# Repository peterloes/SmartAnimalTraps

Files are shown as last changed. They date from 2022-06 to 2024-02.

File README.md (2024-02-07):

# SmartAnimalTraps
Electrical applications for non-deadly animal traps built up with intelligent radio module, drive electronics for servomotors
(flap drive) and drive electronics for different low power light barriers.

Author: Loës P. (2022) 

## 1 RadiomoduleV1.0 & electronicsLightbarriers & electronicsServo
- Radio module V1.0 add-on board (not illustrated)
- Electronic light barriers for different distances.
- Servomotor and shutter is adjusted to the end positions.

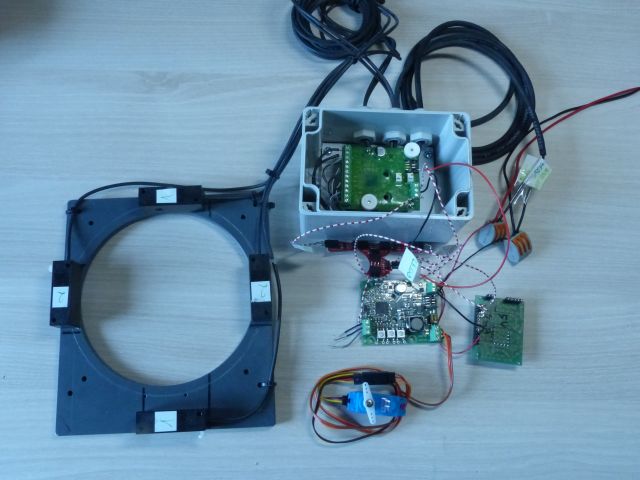
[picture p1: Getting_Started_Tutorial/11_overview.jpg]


The radio handheld transmitter is able to open and close the shutter by pressing a button.

Light barrier 1 and light barrier 2 are connected with logic AND. Both light barriers needs a falling edge of the signals to close the shutter. 
Light barrier 1 and light barrier 2 is forbidden to open the shutter.

Pushbutton 1 and pushbutton 2, mounted on the top of the electronical circuit, are able to open and close the shutter.

### Current consumption:

Standby 20.8mA@6V, clocked approx. 2.0mA@6V (after 10 minutes).

Operate mode 320mA@6V (max.)

### Application bird trap:

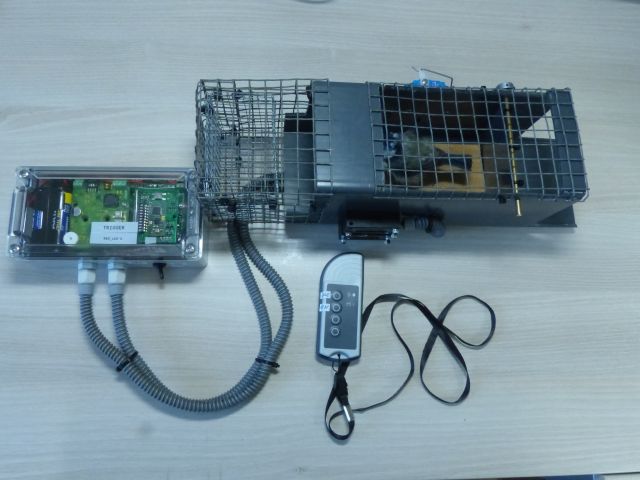
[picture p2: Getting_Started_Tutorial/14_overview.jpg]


### Components:

https://github.com/peterloes/SmartAnimalTraps/blob/main/Getting_Started_Tutorial/13_wireless_radiomodule.JPG

https://github.com/peterloes/SmartAnimalTraps/blob/main/Schematics/radio_module_V1.0.brd.pdf

https://github.com/peterloes/Light_Barrier

https://github.com/peterloes/Servo_Engine

--> Protection against misuse!!! Dear follower, please contact me via email to get more information about the used wireless radio module. 

## 2 RadiomoduleV2.0 & electronicsServo
- Radio module V2.0 add-on board (not illustrated) 
- No light barriers
- Servomotor and shutter is adjusted to the end positions.

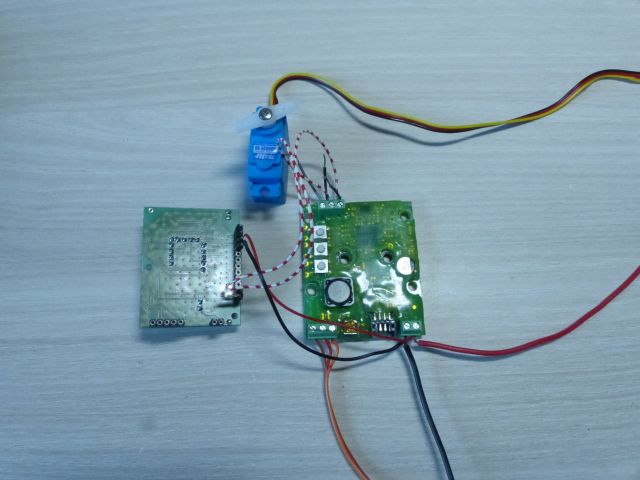
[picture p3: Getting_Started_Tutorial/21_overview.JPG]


The radio handheld transmitter is able to open and close the shutter by pressing a button.

Pushbutton 1 and pushbutton 2, mounted on the top of the electronical circuit, are able to open and close the shutter.

### Current consumption:  

Standby 20.5mA@6V, clocked approx. 2.3mA@6V (after 10 minutes).

Operate mode 235mA@6V (max.)

### Components:

https://github.com/peterloes/SmartAnimalTraps/blob/main/Getting_Started_Tutorial/13_wireless_radiomodule.JPG

https://github.com/peterloes/SmartAnimalTraps/blob/main/Schematics/radio_module_V2.0.brd.pdf

https://github.com/peterloes/Servo_Engine

--> Protection against misuse!!! Dear follower, please contact me via email to get more information about the used wireless radio module. 

## 3 RadiomoduleV3.0 & modifiedServo
- Radio module V3.0 add-on board (Version from year 2010, to revision)
- No light barriers
- Full rotation of modified servomotor --> Motor rotation 360° --> left/right rotations

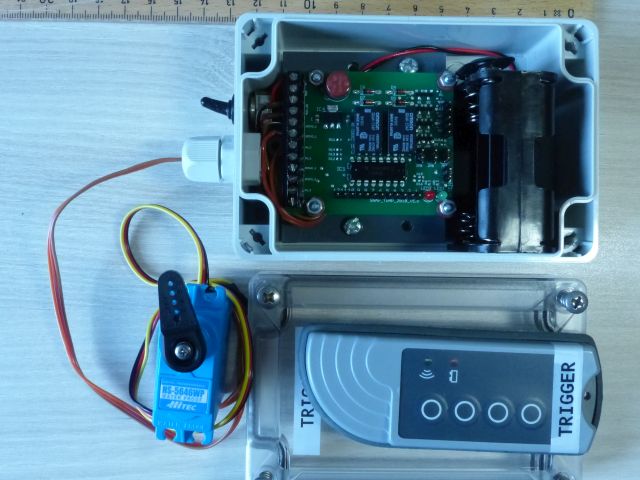
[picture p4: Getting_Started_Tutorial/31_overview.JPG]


The radio handheld transmitter is able to open, close and to rotates the shutter by pressing a button.

### Current consumption:  

Standby 30mA@6V, clocked approx. 11.4mA@6V (after 10 minutes). With LEDs.

Operate mode 179mA@6V Motor is steady turning. With LEDs.

### Application:

https://github.com/peterloes/SmartAnimalTraps/blob/main/Getting_Started_Tutorial/Snaptrap.jpg

### Components:

https://github.com/peterloes/SmartAnimalTraps/blob/main/Getting_Started_Tutorial/13_wireless_radiomodule.JPG

https://github.com/peterloes/SmartAnimalTraps/blob/main/Schematics/radio_module_V3.0.brd.pdf

https://github.com/peterloes/SmartAnimalTraps/blob/main/Getting_Started_Tutorial/33_Servo_modified.JPG

https://github.com/peterloes/SmartAnimalTraps/blob/main/Getting_Started_Tutorial/34_old_batterypack.JPG

--> Protection against misuse!!! Dear follower, please contact me via email to get more information about the used wireless radio module. 

## 4 RadiomoduleV4.0 & reusedFrontplate & electronicsLightbarriers & electronicsServo
- Radio module V4.0 add-on board (not illustrated)
- Reused frontplate from nestbox included light barriers.
- Electronic light barriers.
- Servomotor and shutter is adjusted to the end positions.

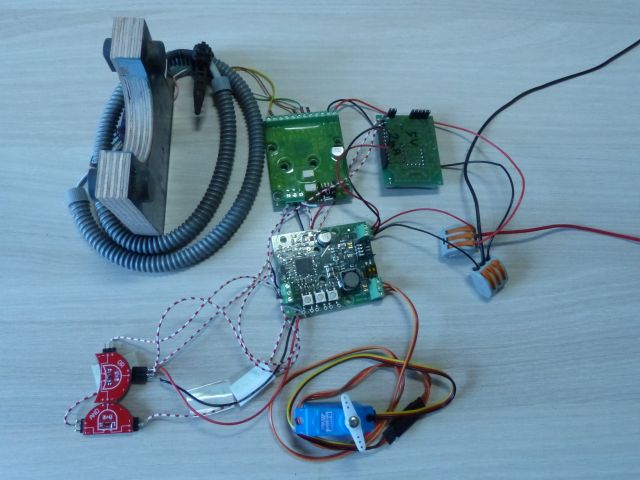
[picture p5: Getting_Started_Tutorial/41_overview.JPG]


The radio handheld transmitter is able to open and close the shutter by pressing a button.

Light barrier 1 and light barrier 2 are connected with logic AND. Both light barriers needs a falling edge of the signals to close the shutter.
Light barrier 1 and light barrier 2 is forbidden to open the shutter.

Pushbutton 1 and pushbutton 2, mounted on the top of the electronical circuit, are able to open and close the shutter.

### Current consumption:

Standby 21.9mA@6V, clocked approx. 3.5mA@6V (after 10 minutes). With LEDs.

Operate mode 303mA@6V (max.). With LEDs.

### Components:

https://github.com/peterloes/SmartAnimalTraps/blob/main/Getting_Started_Tutorial/13_wireless_radiomodule.JPG

https://github.com/peterloes/SmartAnimalTraps/blob/main/Schematics/radio_module_V4.0.brd.pdf

https://github.com/peterloes/Light_Barrier

https://github.com/peterloes/Servo_Engine

Frontplate nestbox

https://github.com/peterloes/RFID-MS

https://github.com/peterloes/SmartAnimalTraps/blob/main/Getting_Started_Tutorial/7_Supplier.txt

--> Protection against misuse!!! Dear follower, please contact me via email to get more information about the used wireless radio module. 

## 5 ElectronicsLightBarriers & electronicsServo
- No radio module
- Electronic light barriers for different distances are switching shutter positions.
- Servomotor and shutter is adjusted to the end positions.

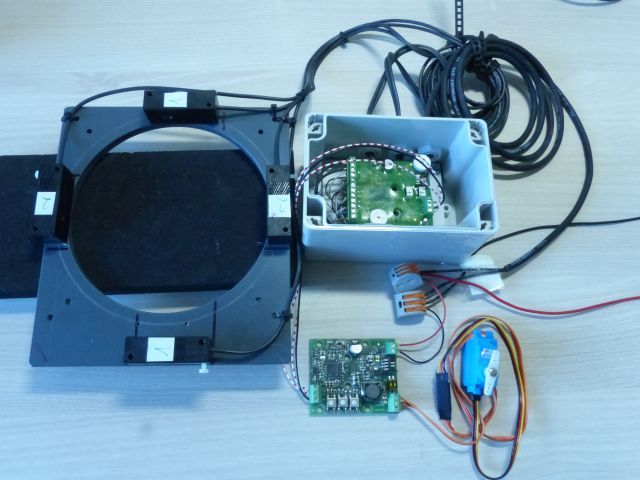
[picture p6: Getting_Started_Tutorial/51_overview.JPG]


Light barrier 1 or light barrier 2 are able to open or to close the shutter.

Pushbutton 1 or pushbutton 2, mounted on the top of the electronical circuit, are able to open or to close the shutter.

### Current consumption:

Standby 0,22mA@6V --> 220µA@6V

Operate mode 322mA@6V (max.)

### Components:

https://github.com/peterloes/Light_Barrier

https://github.com/peterloes/Servo_Engine

## 6 ReusedFrontplate & electronicsServo
- No radio module
- Reused frontplate from nestbox included light barriers. Switching shutter positions.
- Servomotor and shutter is adjusted to the end positions.

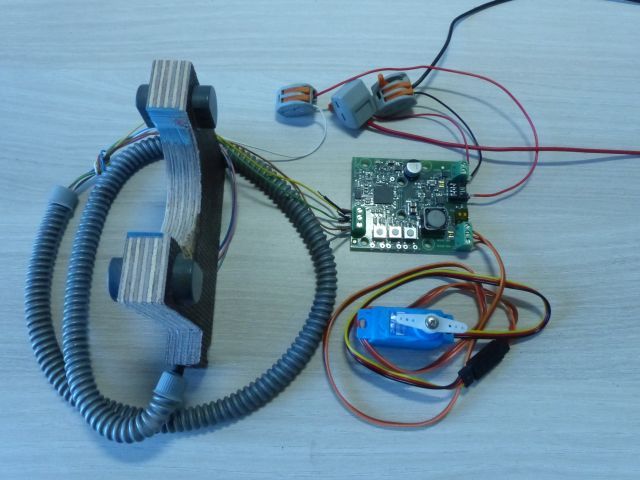
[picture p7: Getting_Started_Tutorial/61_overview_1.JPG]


Light barrier 1 or light barrier 2 are able to open or to close the shutter.

Pushbutton 1 or pushbutton 2, mounted on the top of the electronical circuit, are able to open or to close the shutter.

### Current consumption:

Standby 0,05mA@6V --> 50µA@6V

Operate mode 375mA@6V (max.)

### Components:

https://github.com/peterloes/Servo_Engine

Frontplate nestbox

https://github.com/peterloes/RFID-MS

https://github.com/peterloes/SmartAnimalTraps/blob/main/Getting_Started_Tutorial/7_Supplier.txt

### EXTENSIONS

https://github.com/peterloes/SmartAnimalTraps/blob/main/Getting_Started_Tutorial/SailwinchServo.jpg

https://github.com/peterloes/SmartAnimalTraps/blob/main/Getting_Started_Tutorial/LightBarrier_example.jpg

https://hackaday.io/project/193448-solenoid-as-a-switch-with-proximity-detection

#### Intelligent radio module:

Wireless module receives and evaluates the data received from a transmitter.

In order to carry out a command from a transmitter, it must first be taught.
Teaching of a transmitter is carried out very easily by means of a button.
As required, up to 60 transmitters can be taught with all keys or individual transmission keys.
The particular highlight is the feedback from the receiver. You can see from the transmitter
whether the wireless communication was successful and receive information about the quality of the transmission path.
Electronical release range of 70 metres tested in urban environment. 

https://github.com/peterloes/SmartAnimalTraps/blob/main/Getting_Started_Tutorial/13_wireless_radiomodule.JPG

Examples after teaching the modules:
 
Hand-held transmitter --> Button1 -- Trap1 --> Shutter closed

Hand-held transmitter --> Button2 -- Trap1 --> Shutter open

Hand-held transmitter --> Button3 -- Trap2 --> Shutter closed

Hand-held transmitter --> Button4 -- Trap2 --> Shutter open

or 
 
Hand-held transmitter --> Button1 -- Trap1-Trap2-Trap3-Trap4 --> Shutter closed

Hand-held transmitter --> Button2 -- Trap1-Trap2-Trap3-Trap4 --> Shutter open

#### Drive electronics for servomotor and flap:

Trigger always the same positions over input signals (two end points) or over pushbuttons.

The servo setup procedure consists of 4 steps:

Adjust end position 1. This can be the most left or the most right end point. This position will be reached after power-up if valid servo data has been found in FLASH.
Adjust end position 2. This is the opposite end position to position 1.
Adjust servo speed. The servo permanently moves between the two end points. The speed can be adjusted via S1 and S2.
Asserting S3 the 4th time stores the servo parameters into FLASH and returns to normal operation

.https://github.com/peterloes/Servo_Engine

Examples for shutter positions after adjust the end positions:

Pushbutton 1 end position 1 --> Shutter open 

Pushbutton 2 end position 2 --> Shutter closed

or

Input signal 1 end position 1 --> Shutter open

Input signal 2 end position 2 --> Shutter closed

#### Drive electronics for light barriers:

Supported two low power light barriers, adjustable for different distances(size of animal) 10 centimetres to tested 3.3 metres. 
The beam is scattered light independently and invisible.
Wide power input range of light barrier circuit board 3.3V to max.60V. Used receiver from Vishay "TSSP58038" and LED from Vishay "VSLB3940"

https://github.com/peterloes/Light_Barrier

Examples for light barriers:

Light barrier 1 and light barrier 2 are connected with logic AND. Both light barriers needs a falling edge of the signals to close the shutter.

Light barrier 1 or light barrier 2 are able to open or to close the shutter.

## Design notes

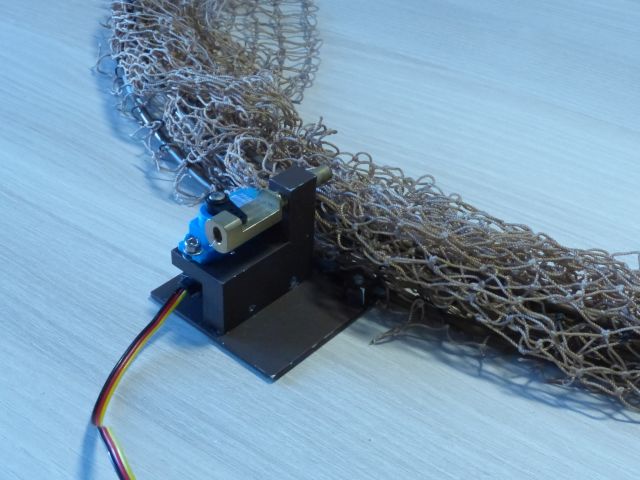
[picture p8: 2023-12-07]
Getting_Started_Tutorial/91_overview_1.JPG

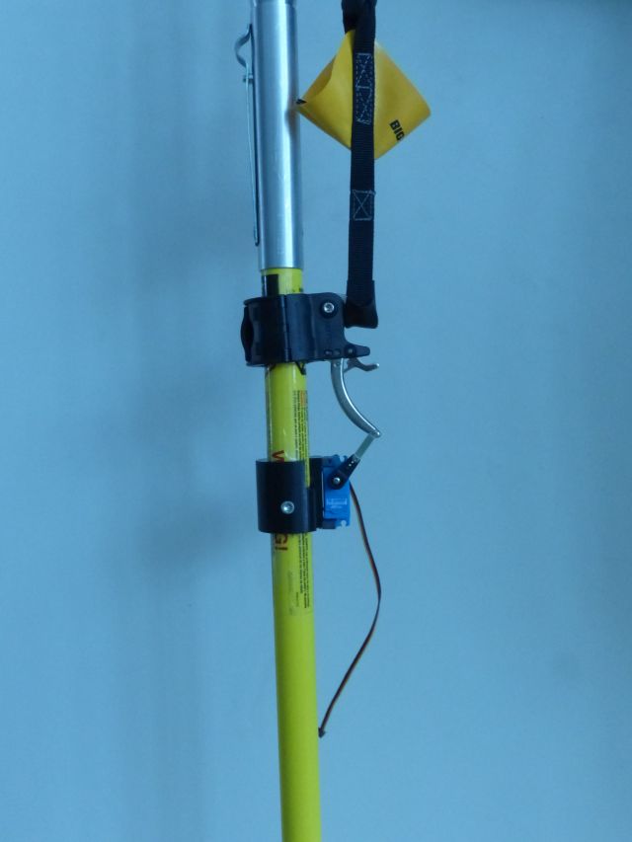
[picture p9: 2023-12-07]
Getting_Started_Tutorial/81_overview_1.JPG

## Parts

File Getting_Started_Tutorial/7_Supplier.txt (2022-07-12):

Lightbarriers for front plate nestbox
Doppel - Lichtschranke Art.Nr. P00700 (Lichtschranken in Frontplatten):

SWISSSENSOR AG
Geschäftsleitung Hermann Beer

Steinacherstrasse 4
CH-9327 Tübach
Germany
Tel. +41(0)71 845 24 24
mailto:beer@swisssensor.ch
www.swisssensor.ch

Supplier of all Electronic Boards

Top-Print Electronic GmbH
Oskar Schmid

Rosenheimer Landstr. 129a
85521 Ottobrunn
Germany
Tel.: +49-89-60668047
Fax: +49-89-60668049
mailto: info@top-print.eu
https://www.leiterplatten-muenchen.de/

Housing
https://www.spelsberg.de/industrieleergehaeuse/glatt-mit-befestigungsnocken/10100401/
TG ABS 1208-6-to
Artikelnummer: 10100401 | Maße: 122 x 82 x 55 mm
Leergehäuse IP66 / IP67 Polycarbonat

HS-5646WP HV Standard Waterproof MG BB
5000-SeriesStandardDigitalServo
https://www.hitecservos.com/product/HS-5646WP/hs-5646wp-digital-standard-programmable-waterproof-servo

HS-5086WP Metal Gear, Micro Digital Waterproof Servo
https://hitecrcd.com/products/servos/digital/d-series/hs-5086wp/product

Features
Metal Gear with MP First Gear
Top Ball Bearings
3-Pole Cored Ferrite Motor
Industry's First IP67-Rated Waterproof Case*
Programmable Circuit
International Protection Code
Dust Tight and Immersion up to 1M

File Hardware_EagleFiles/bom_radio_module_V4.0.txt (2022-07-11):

Stückliste exportiert aus C:/MPIO/TECHNIK/HARDWARE/EAGLE_FILES/Wireless_Servo_2022/radio_module_V4.0.sch am 11.07.2022 12:27

Part Value              Device       Package Description                                              
C1   100n(n.b.)         C-EUC0805    C0805   CAPACITOR, European symbol                               
C2   100n               C-EUC0805    C0805   CAPACITOR, European symbol                               
C3   100n               C-EUC0805    C0805   CAPACITOR, European symbol                               
C4   100n               C-EUC0805    C0805   CAPACITOR, European symbol                               
IC1  74AHC1G04DBV(n.b.) 74AHC1G04DBV SOT23-5 INVERTER Gate                                            
IC2  74AHC1G04DBV(n.b.) 74AHC1G04DBV SOT23-5 INVERTER Gate                                            
IC3  74AHC1G08DBV       74AHC1G08DBV SOT23-5 2-input AND gate                                         
IC4  74AHC1G32DBV       74AHC1G32DBV SOT23-5 2-input OR gate                                          
JP1                     PINHD-1X2    1X02    PIN HEADER                                               
JP2                     PINHD-1X5    1X05    PIN HEADER                                               
JP3                     PINHD-1X12   1X12    PIN HEADER                                               
JP4  (n.b.)             PINHD-1X2    1X02    PIN HEADER                                               
R1   100k(n.b.)         R-EU_R0805   R0805   RESISTOR, European symbol                                
R2   100k(n.b.)         R-EU_R0805   R0805   RESISTOR, European symbol                                
R3   100k(n.b.)         R-EU_R0805   R0805   RESISTOR, European symbol                                
R4   100k(n.b.)         R-EU_R0805   R0805   RESISTOR, European symbol                                
R5   100k(n.b.)         R-EU_R0805   R0805   RESISTOR, European symbol                                
R6   0                  R-EU_R0805   R0805   RESISTOR, European symbol                                
R7   0                  R-EU_R0805   R0805   RESISTOR, European symbol                                
X1   MKDS1/2-3,81       MKDS1/2-3,81 2POL381 MKDS 1/2-3,81 - Order No. 1727010 (RS-Online - 101-5384) 
X2   MKDS1/3-3,81       MKDS1/3-3,81 3POL381 MKDS 1/3-3,81 - Order No. 1727023 (RS-Online - 101-5390) 
X3   MKDS1/3-3,81       MKDS1/3-3,81 3POL381 MKDS 1/3-3,81 - Order No. 1727023 (RS-Online - 101-5390) 
X4   MKDS1/4-3,81       MKDS1/4-3,81 4POL381 MKDS 1/4-3,81 - Order No. 1727036

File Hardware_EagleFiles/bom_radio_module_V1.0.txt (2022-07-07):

Stückliste exportiert aus C:/MPIO/TECHNIK/HARDWARE/EAGLE_FILES/Wireless_Servo_2022/radio_module_V1.0.sch am 07.07.2022 10:13

Part Value        Device       Package Description                                              
C1   100n         C-EUC0805    C0805   CAPACITOR, European symbol                               
C2   100n         C-EUC0805    C0805   CAPACITOR, European symbol                               
C3   100n         C-EUC0805    C0805   CAPACITOR, European symbol                               
C4   100n         C-EUC0805    C0805   CAPACITOR, European symbol                               
IC1  74AHC1G04DBV 74AHC1G04DBV SOT23-5 INVERTER Gate                                            
IC2  74AHC1G04DBV 74AHC1G04DBV SOT23-5 INVERTER Gate                                            
IC3  74AHC1G08DBV 74AHC1G08DBV SOT23-5 2-input AND gate                                         
IC4  74AHC1G32DBV 74AHC1G32DBV SOT23-5 2-input OR gate                                          
JP1               PINHD-1X2    1X02    PIN HEADER (Pin Strip Header Single 2.54mm Herst.: 929834-01-36-RK)                                              
JP2               PINHD-1X5    1X05    PIN HEADER (Pin Strip Header Single 2.54mm Herst.: 929834-01-36-RK)                                              
JP3               PINHD-1X12   1X12    PIN HEADER (Pin Strip Header Single 2.54mm Herst.: 929834-01-36-RK)                                              
JP4  (n.b.)       PINHD-1X2    1X02    PIN HEADER                                               
R1   100k(n.b.)   R-EU_R0805   R0805   RESISTOR, European symbol                                
R2   100k(n.b.)   R-EU_R0805   R0805   RESISTOR, European symbol                                
R3   100k(n.b.)   R-EU_R0805   R0805   RESISTOR, European symbol                                
R4   100k(n.b.)   R-EU_R0805   R0805   RESISTOR, European symbol                                
R5   100k(n.b.)   R-EU_R0805   R0805   RESISTOR, European symbol                                
X1   MKDS1/2-3,81 MKDS1/2-3,81 2POL381 MKDS 1/2-3,81 - Order No. 1727010 (RS-Online - 101-5384) 
X2   MKDS1/3-3,81 MKDS1/3-3,81 3POL381 MKDS 1/3-3,81 - Order No. 1727023 (RS-Online - 101-5390) 
X3   MKDS1/3-3,81 MKDS1/3-3,81 3POL381 MKDS 1/3-3,81 - Order No. 1727023 (RS-Online - 101-5390) 
X4   MKDS1/4-3,81 MKDS1/4-3,81 4POL381 MKDS 1/4-3,81 - Order No. 1727036

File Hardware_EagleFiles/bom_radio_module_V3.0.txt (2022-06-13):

Part    Value             Device               Package   Description                                                   
1       NC                1,6/0,9              1,6/0,9   THROUGH-HOLE PAD Pin Strip Header Single 2.54mm Herst.: 929834-01-36-RK                                              
2       NC                1,6/0,9              1,6/0,9   THROUGH-HOLE PAD                                              
3       NC                1,6/0,9              1,6/0,9   THROUGH-HOLE PAD                                              
4       NC                1,6/0,9              1,6/0,9   THROUGH-HOLE PAD                                              
5       NC                1,6/0,9              1,6/0,9   THROUGH-HOLE PAD                                              
6       NC                1,6/0,9              1,6/0,9   THROUGH-HOLE PAD                                              
7       NC                1,6/0,9              1,6/0,9   THROUGH-HOLE PAD                                              
8       NC                1,6/0,9              1,6/0,9   THROUGH-HOLE PAD                                              
9       GND               1,6/0,9              1,6/0,9   THROUGH-HOLE PAD                                              
10      +U (4...14v)      1,6/0,9              1,6/0,9   THROUGH-HOLE PAD                                              
11      NC                1,6/0,9              1,6/0,9   THROUGH-HOLE PAD                                              
12      NC                1,6/0,9              1,6/0,9   THROUGH-HOLE PAD                                              
ANTENNA WIREPAD           1,6/0,9              1,6/0,9   THROUGH-HOLE PAD                                              
C1      10µF/6.3V         C-EUC0805            C0805     CAPACITOR, European symbol                                    
C2      10µF/6.3V         C-EUC0805            C0805     CAPACITOR, European symbol                                    
D0      WIREPAD           1,6/0,9              1,6/0,9   THROUGH-HOLE PAD Pin Strip Header Single 2.54mm Herst.: 929834-01-36-RK                                             
D1      WIREPAD           1,6/0,9              1,6/0,9   THROUGH-HOLE PAD                                              
D2      WIREPAD           1,6/0,9              1,6/0,9   THROUGH-HOLE PAD                                              
D3      WIREPAD           1,6/0,9              1,6/0,9   THROUGH-HOLE PAD                                              
D4      1N4148            1N4148DO35-7         DO35-7    DIODE                                                         
D5      1N4148            1N4148DO35-7         DO35-7    DIODE                                                         
D6      1N4148            1N4148DO35-7         DO35-7    DIODE                                                         
D7      1N4148            1N4148DO35-7         DO35-7    DIODE                                                         
F1      800mA Flink       FUSE19560            19560     Fuse                                                          
GD      WIREPAD           1,6/0,9              1,6/0,9   THROUGH-HOLE PAD                                              
IC1     L293D             L293D                DIL16     PUSH-PULL 4 CHANNEL DRIVER                                    
IC2     G5AK-234P         G5AK-234P            G5AK-234P                                                               
IC3     G5AK-234P         G5AK-234P            G5AK-234P                                                               
IC4     ADP3338AKCZ       LD117AS12TR          SOT223    Low drop fixed and adjustable positive voltage regulators 1 A 
JP7     Dauerbetrieb      JP1E                 JP1       JUMPER                                                        
JP8     SW_1              JP1E                 JP1       JUMPER                                                        
JP9     SW_2              JP1E                 JP1       JUMPER                                                        
LED1    Green low current LED3MM               LED3MM    LED                                                           
LED2    Red low current   LED3MM               LED3MM    LED                                                           
Q1      BCW30             PNP-TRANSISTOR_SOT23 SOT23     PNP TRANSISTOR                                                
Q2      BCW30             PNP-TRANSISTOR_SOT23 SOT23     PNP TRANSISTOR                                                
Q3      BCW30             PNP-TRANSISTOR_SOT23 SOT23     PNP TRANSISTOR                                                
Q4      BCW30             PNP-TRANSISTOR_SOT23 SOT23     PNP TRANSISTOR                                                
Q5      BCW30             PNP-TRANSISTOR_SOT23 SOT23     PNP TRANSISTOR                                                
Q6      BCW30             PNP-TRANSISTOR_SOT23 SOT23     PNP TRANSISTOR                                                
Q7      BCW30             PNP-TRANSISTOR_SOT23 SOT23     PNP TRANSISTOR                                                
Q8      BCW30             PNP-TRANSISTOR_SOT23 SOT23     PNP TRANSISTOR                                                
R1      1k                R-EU_R0402           R0402     RESISTOR, European symbol                                     
R2      1k                R-EU_R0402           R0402     RESISTOR, European symbol                                     
R3      1k                R-EU_R0402           R0402     RESISTOR, European symbol                                     
R4      1k                R-EU_R0402           R0402     RESISTOR, European symbol                                     
R5      1k                R-EU_R0402           R0402     RESISTOR, European symbol                                     
R6      1k                R-EU_R0402           R0402     RESISTOR, European symbol                                     
R7      1k                R-EU_R0402           R0402     RESISTOR, European symbol                                     
R8      1k                R-EU_R0402           R0402     RESISTOR, European symbol                                     
R9      1k                R-EU_R0402           R0402     RESISTOR, European symbol                                     
R10     1k                R-EU_R0402           R0402     RESISTOR, European symbol                                     
R11     10k               R-EU_R0402           R0402     RESISTOR, European symbol                                     
R12     10k               R-EU_R0402           R0402     RESISTOR, European symbol                                     
R13     10k               R-EU_R0402           R0402     RESISTOR, European symbol                                     
R14     10k               R-EU_R0402           R0402     RESISTOR, European symbol                                     
R15     10k               R-EU_R0402           R0402     RESISTOR, European symbol                                     
R16     10k               R-EU_R0402           R0402     RESISTOR, European symbol                                     
VT      WIREPAD           1,6/0,9              1,6/0,9   THROUGH-HOLE PAD Pin Strip Header Single 2.54mm Herst.: 929834-01-36-RK                                             
X1      MKDS1/12-3,81     MKDS1/12-3,81        12POL381  MKDS 1/12-3,81 - Order No. 1727117

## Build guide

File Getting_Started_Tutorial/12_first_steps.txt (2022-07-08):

Servomotor electronics

Logic module is wired to S2.
Radiomodule(D1_CMOS) is wired to S1.

Circuit board: https://github.com/peterloes/SmartAnimalTraps/blob/main/Schematics/radio_module_V1.0.sch.pdf

Shutter will be at the beginning always closed!

1. Programming servomotor position shutter open
2. Programming servomotor position shutter closed
3. Shutter speed

- Reconnect the servo electronic-board -- > Shutter should move to closed.
- Press hand-held transmitter button 2 for open the shutter.

hand-held transmitter

- Button 1 is to close the shutter.
- Button 2 is to open the shutter.

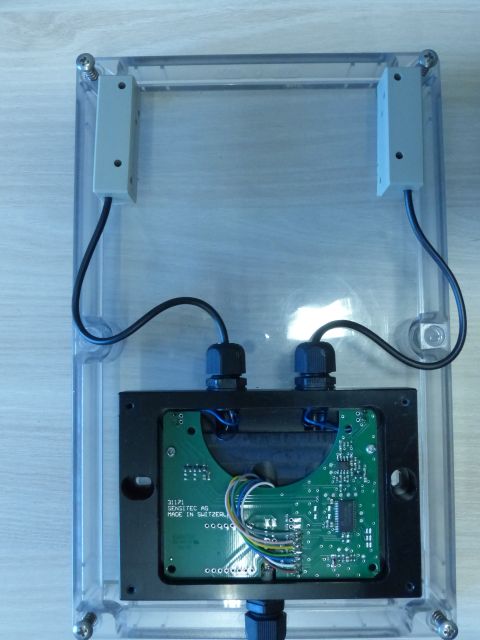
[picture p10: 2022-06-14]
Getting_Started_Tutorial/LightBarrier_example.jpg

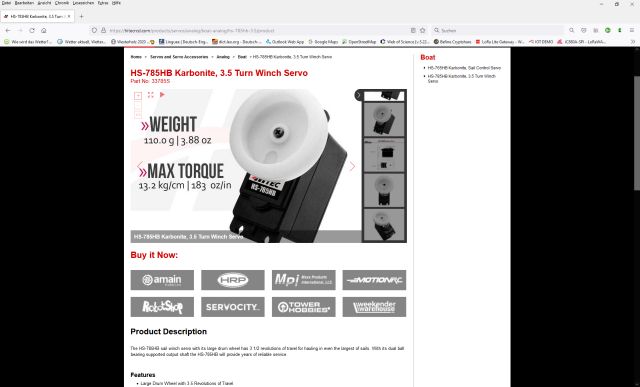
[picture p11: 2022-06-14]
Getting_Started_Tutorial/SailwinchServo.jpg

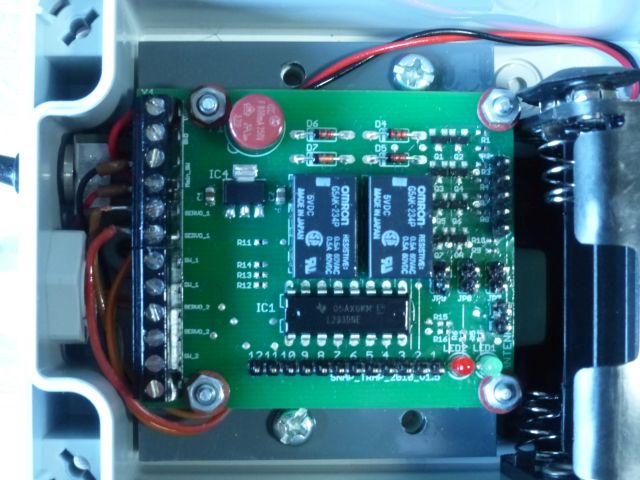
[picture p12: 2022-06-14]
Getting_Started_Tutorial/32_RadioModule_V1.5.JPG

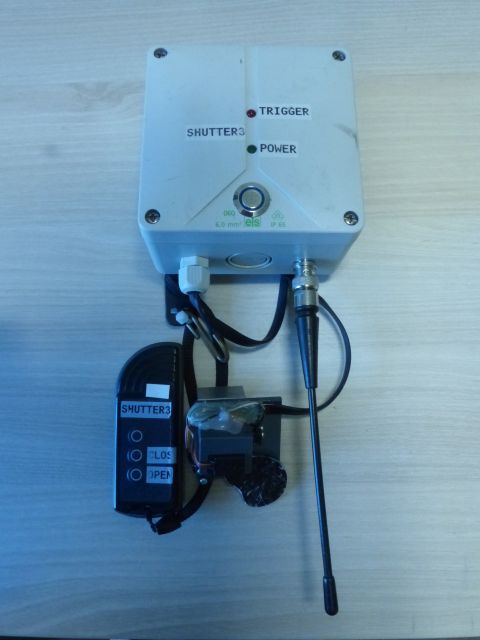
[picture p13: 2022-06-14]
Getting_Started_Tutorial/Snaptrap.jpg

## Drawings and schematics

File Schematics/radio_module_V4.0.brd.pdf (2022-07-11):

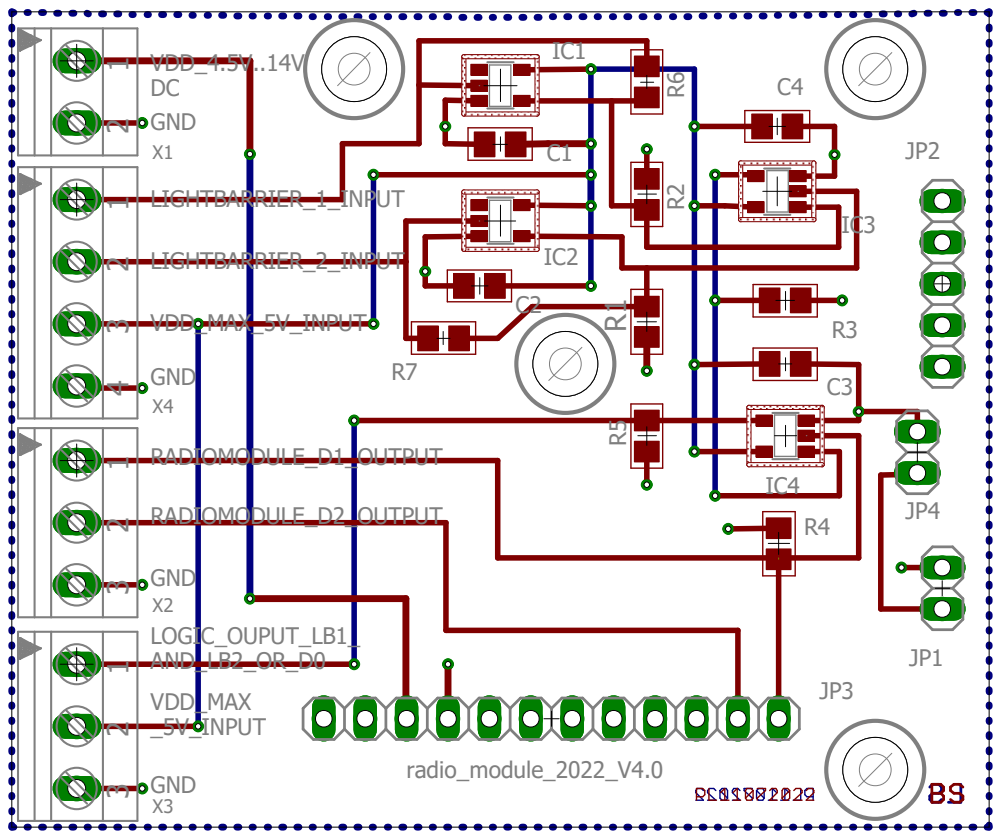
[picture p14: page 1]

12 123 1234 123 radio_module_2022_V4.0 GND VDD_4.5V..14V DCRADIOMODULE_D1_OUTPUT GND RADIOMODULE_D2_OUTPUT GND LIGHTBARRIER_1_INPUT LIGHTBARRIER_2_INPUT VDD_MAX_5V_INPUT GND VDD_MAX _5V_INPUT LOGIC_OUPUT_LB1_ AND_LB2_OR_D0 X1X2 JP1 JP2 JP3 IC1 IC2 IC3 IC4

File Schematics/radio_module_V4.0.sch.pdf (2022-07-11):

# power input

logic power and logic output | logic

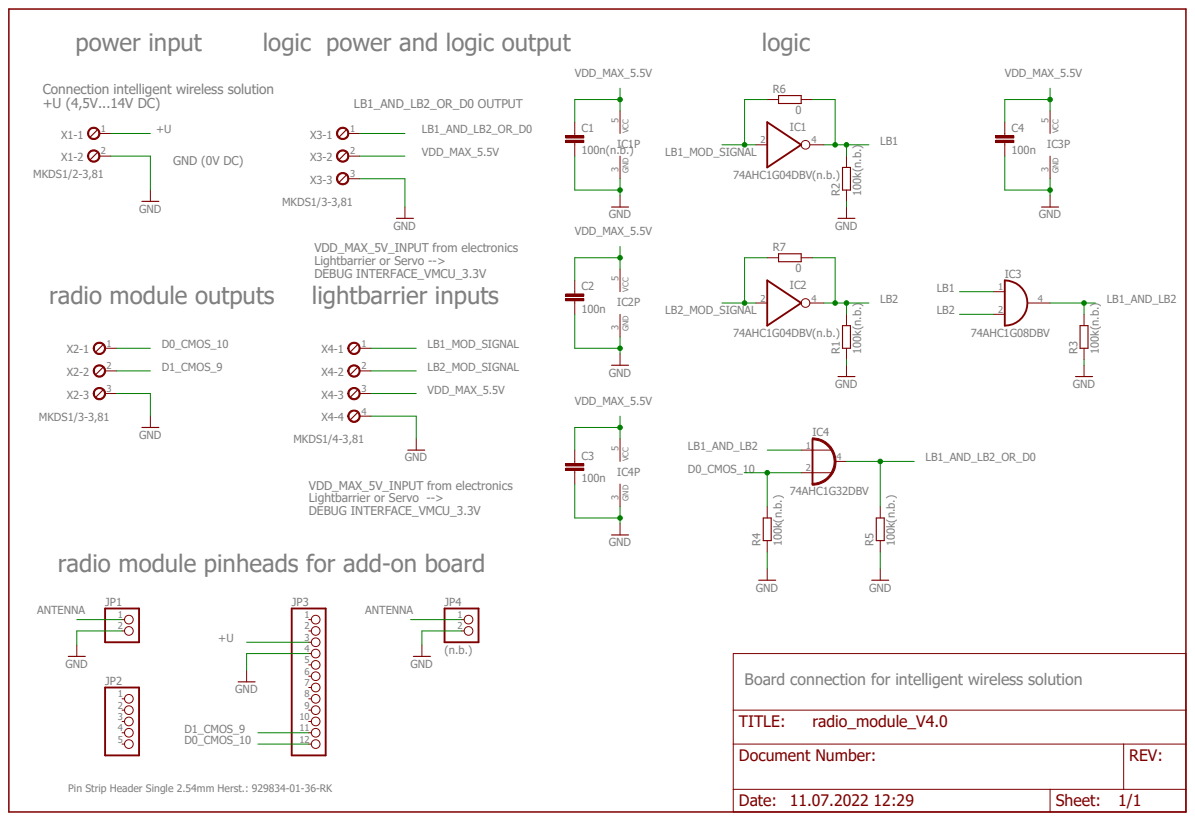
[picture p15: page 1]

Connection intelligent wireless solution

radio module pinheads for add-on board

Board connection for intelligent wireless solution

Document Number: | REV:

Pin Strip Header Single 2.54mm Herst.: 929834-01-36-RK

Date: 11.07.2022 12:29 | Sheet: 1/1

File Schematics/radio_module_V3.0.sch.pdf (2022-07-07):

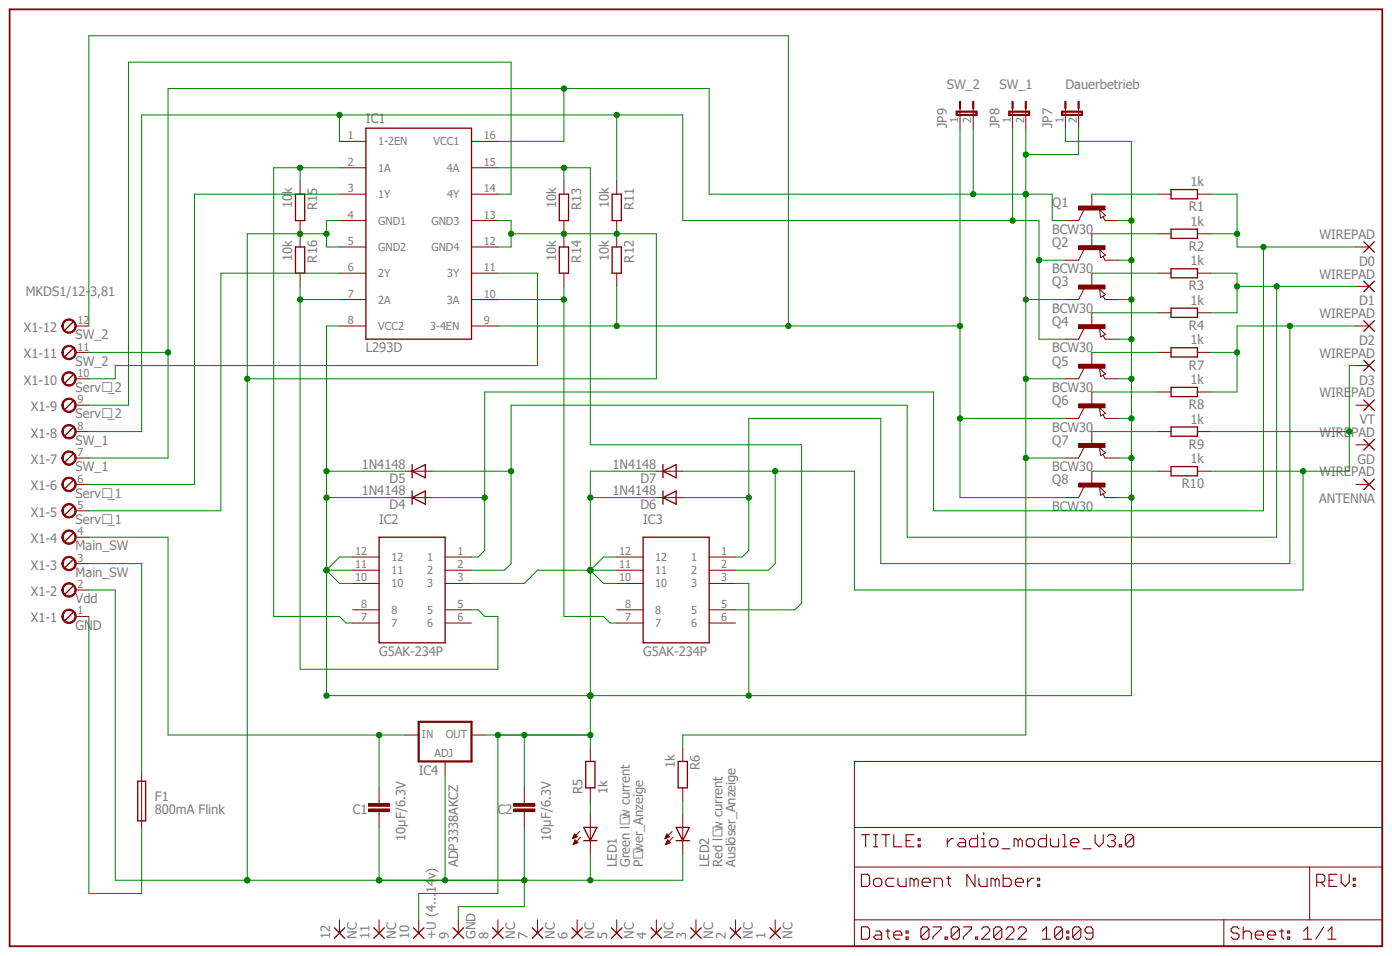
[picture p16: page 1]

Red low current 800mA Flink

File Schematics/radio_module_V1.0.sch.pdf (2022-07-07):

# power input

logic power and logic output | logic

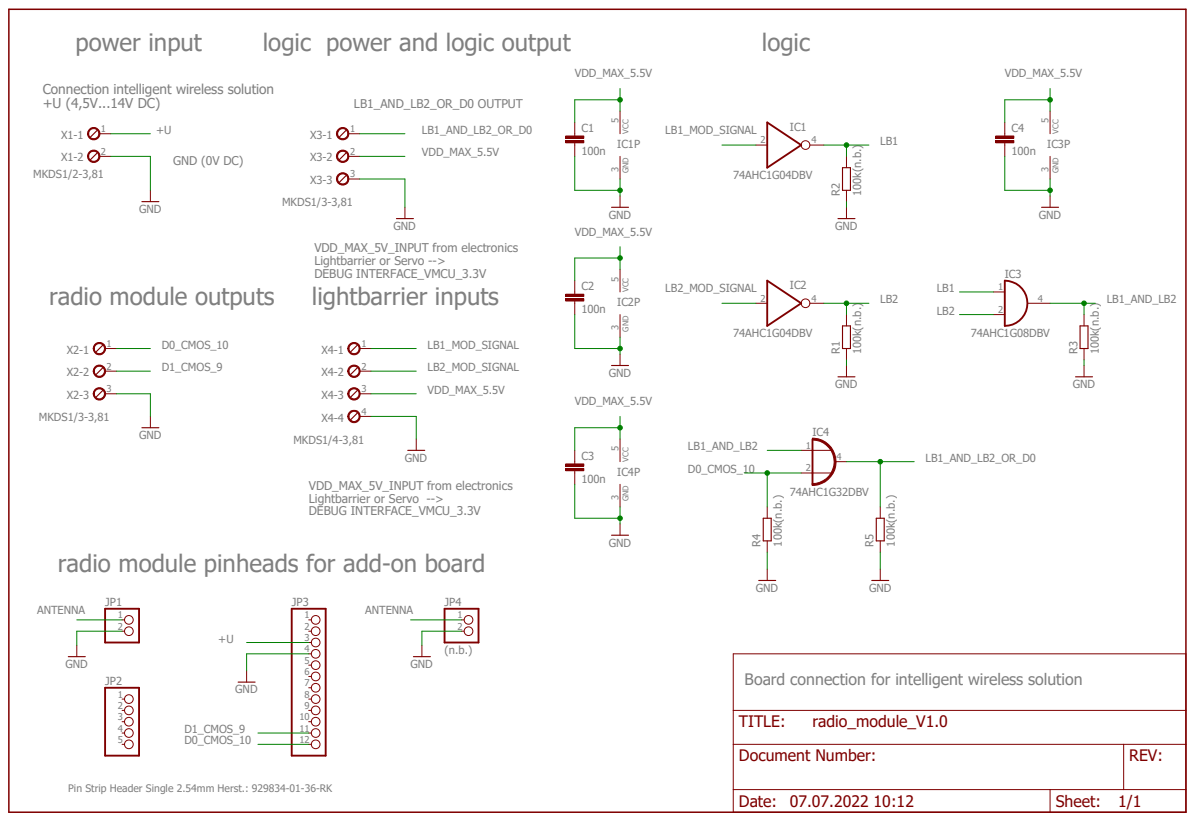
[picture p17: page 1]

Connection intelligent wireless solution

radio module pinheads for add-on board

Board connection for intelligent wireless solution

Document Number: | REV:

Pin Strip Header Single 2.54mm Herst.: 929834-01-36-RK

Date: 07.07.2022 10:12 | Sheet: 1/1

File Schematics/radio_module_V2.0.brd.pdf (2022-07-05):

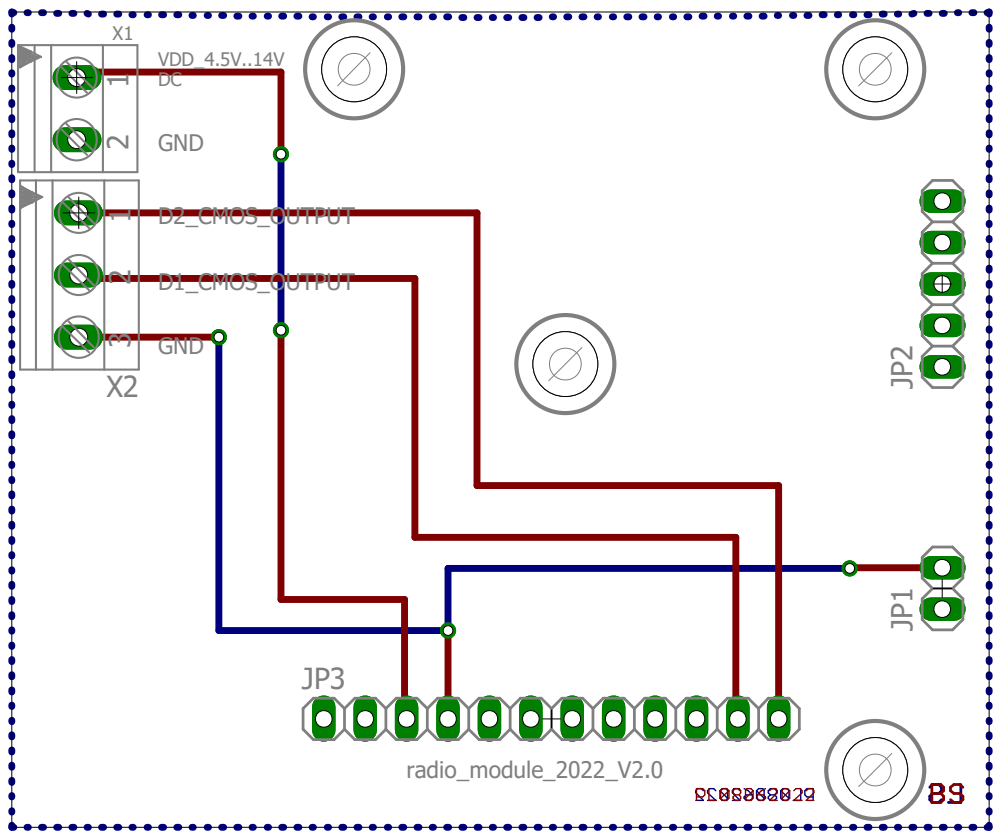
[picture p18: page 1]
radio_module_2022_V2.0; GND; VDD_4.5V..14V DC; D1_CMOS_OUTPUT; D2_CMOS_OUTPUT

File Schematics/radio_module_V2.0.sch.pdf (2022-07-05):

## Pin Description

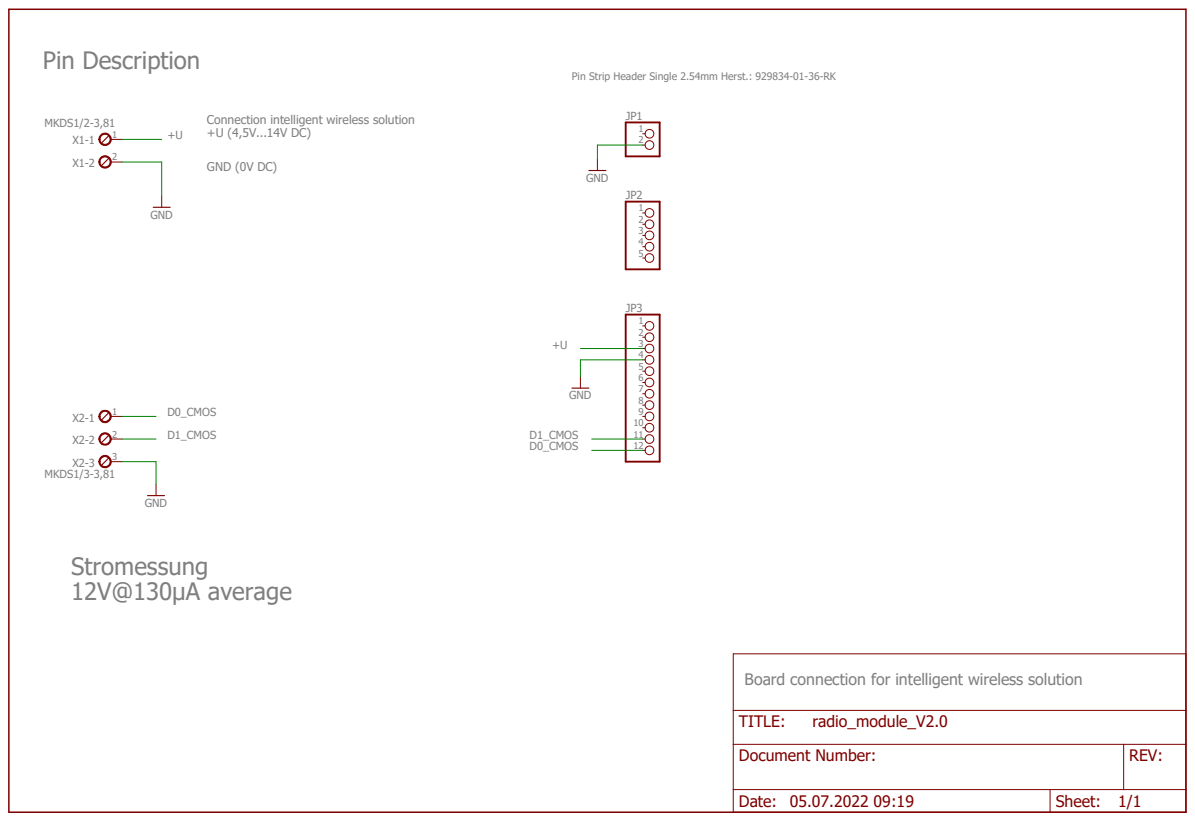
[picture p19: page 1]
Stromessung 12V@130µA average; GND (0V DC); GND; MKDS1/2-3,81; MKDS1/3-3,81; D0_CMOS; D1_CMOS; TITLE:; radio_module_V2.0

Pin Strip Header Single 2.54mm Herst.: 929834-01-36-RK

Connection intelligent wireless solution

Board connection for intelligent wireless solution

Document Number: | REV:

Date: 05.07.2022 09:19 | Sheet: 1/1

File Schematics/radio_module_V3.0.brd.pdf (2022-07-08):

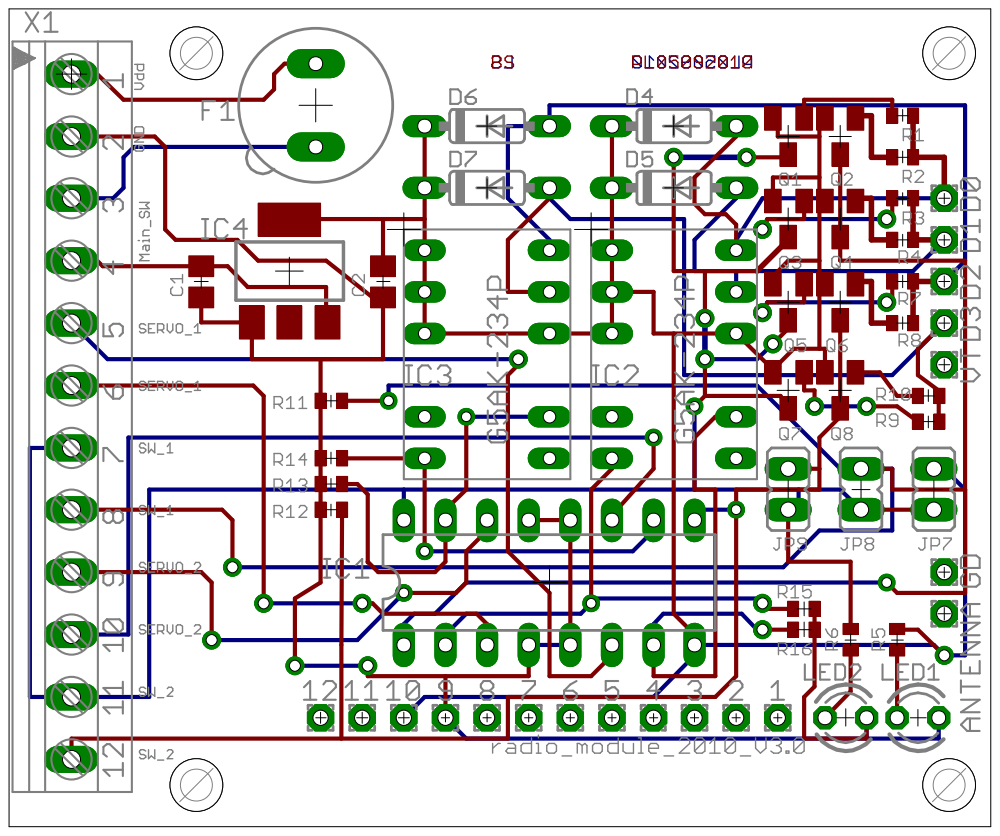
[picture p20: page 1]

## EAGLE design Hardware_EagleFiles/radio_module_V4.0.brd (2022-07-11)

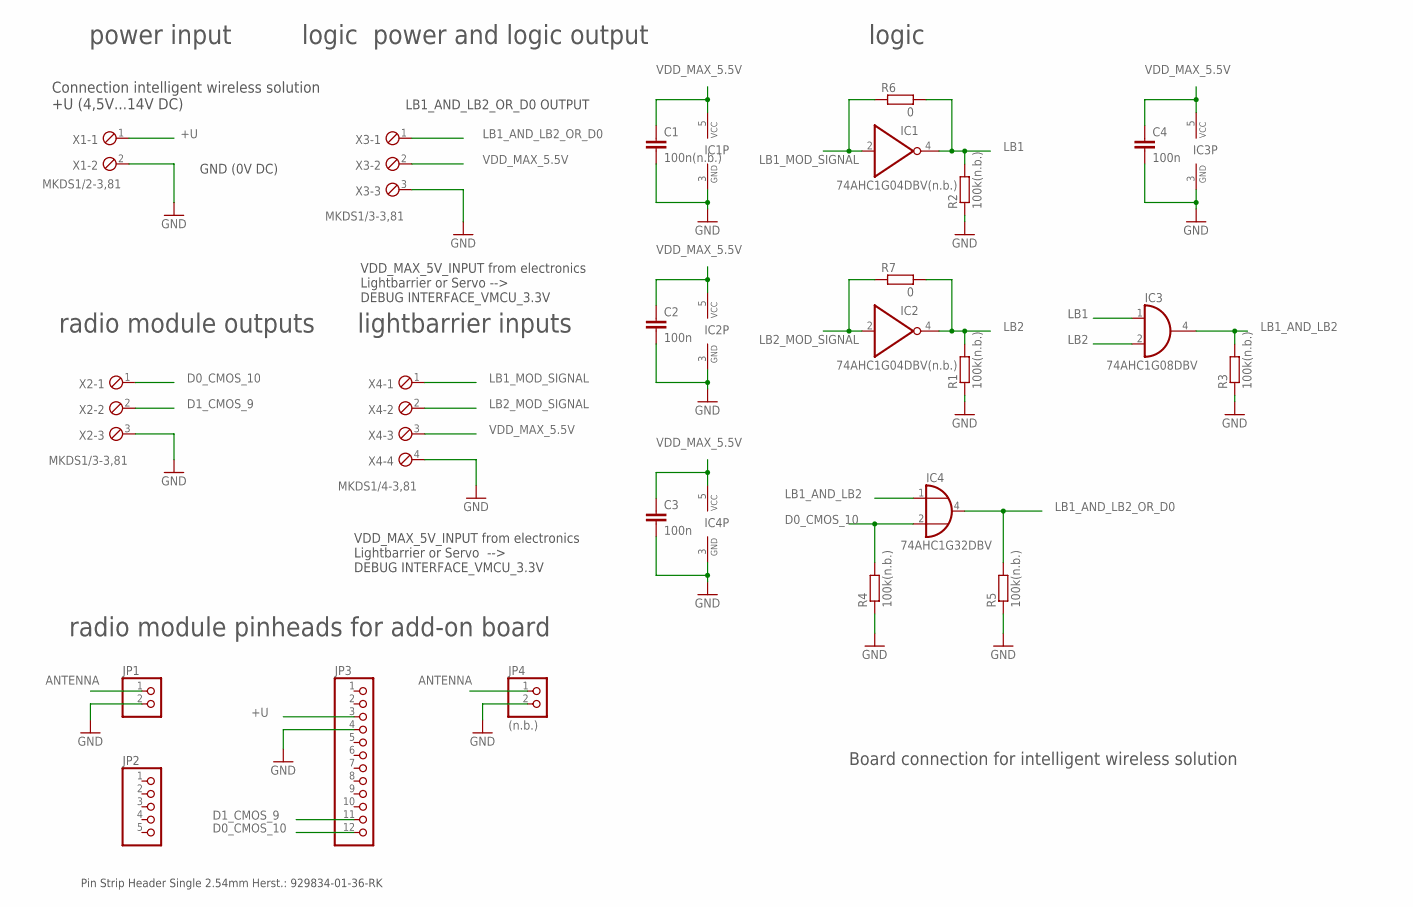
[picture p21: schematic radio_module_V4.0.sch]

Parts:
C1: 100n(n.b.); C0805
C2, C3, C4: 100n; C0805
IC1, IC2: 74AHC1G04DBV(n.b.); SOT23-5
IC3: 74AHC1G08DBV; SOT23-5
IC4: 74AHC1G32DBV; SOT23-5
JP1: PINHD-1X2; 1X02
JP2: PINHD-1X5; 1X05
JP3: PINHD-1X12; 1X12
JP4: (n.b.); 1X02
R1, R2, R3, R4, R5: 100k(n.b.); R0805
R6, R7: 0; R0805
X1: MKDS1/2-3,81; 2POL381
X2, X3: MKDS1/3-3,81; 3POL381
X4: MKDS1/4-3,81; 4POL381

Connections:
+U: JP3.3, X1.1
ANTENNA: JP1.1, JP4.1
D0_CMOS_10: IC4.2 (I1), JP3.12, R4.2, X2.1
D1_CMOS_9: JP3.11, X2.2
GND: C1.2, C2.2, C3.2, C4.2, IC1.3 (GND), IC2.3 (GND), IC3.3 (GND), IC4.3 (GND), JP1.2, JP3.4, JP4.2, R1.1, R2.1, R3.1, R4.1, R5.1, X1.2, X2.3, X3.3, X4.4
LB1: IC1.4 (O), IC3.1 (I0), R2.2, R6.2
LB1_AND_LB2: IC3.4 (O), IC4.1 (I0), R3.2
LB1_AND_LB2_OR_D0: IC4.4 (O), R5.2, X3.1
LB1_MOD_SIGNAL: IC1.2 (I), R6.1, X4.1
LB2: IC2.4 (O), IC3.2 (I1), R1.2, R7.2
LB2_MOD_SIGNAL: IC2.2 (I), R7.1, X4.2
VDD_MAX_5.5V: C1.1, C2.1, C3.1, C4.1, IC1.5 (VCC), IC2.5 (VCC), IC3.5 (VCC), IC4.5 (VCC), X3.2, X4.3

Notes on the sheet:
Board connection for intelligent wireless solution
power input
Connection intelligent wireless solution +U (4,5V...14V DC)
GND (0V DC)
Pin Strip Header Single 2.54mm Herst.: 929834-01-36-RK
radio module pinheads for add-on board
radio module outputs
lightbarrier inputs
logic power and logic output
logic
LB1_AND_LB2_OR_D0 OUTPUT
VDD_MAX_5V_INPUT from electronics Lightbarrier or Servo --> DEBUG INTERFACE_VMCU_3.3V
VDD_MAX_5V_INPUT from electronics Lightbarrier or Servo --> DEBUG INTERFACE_VMCU_3.3V

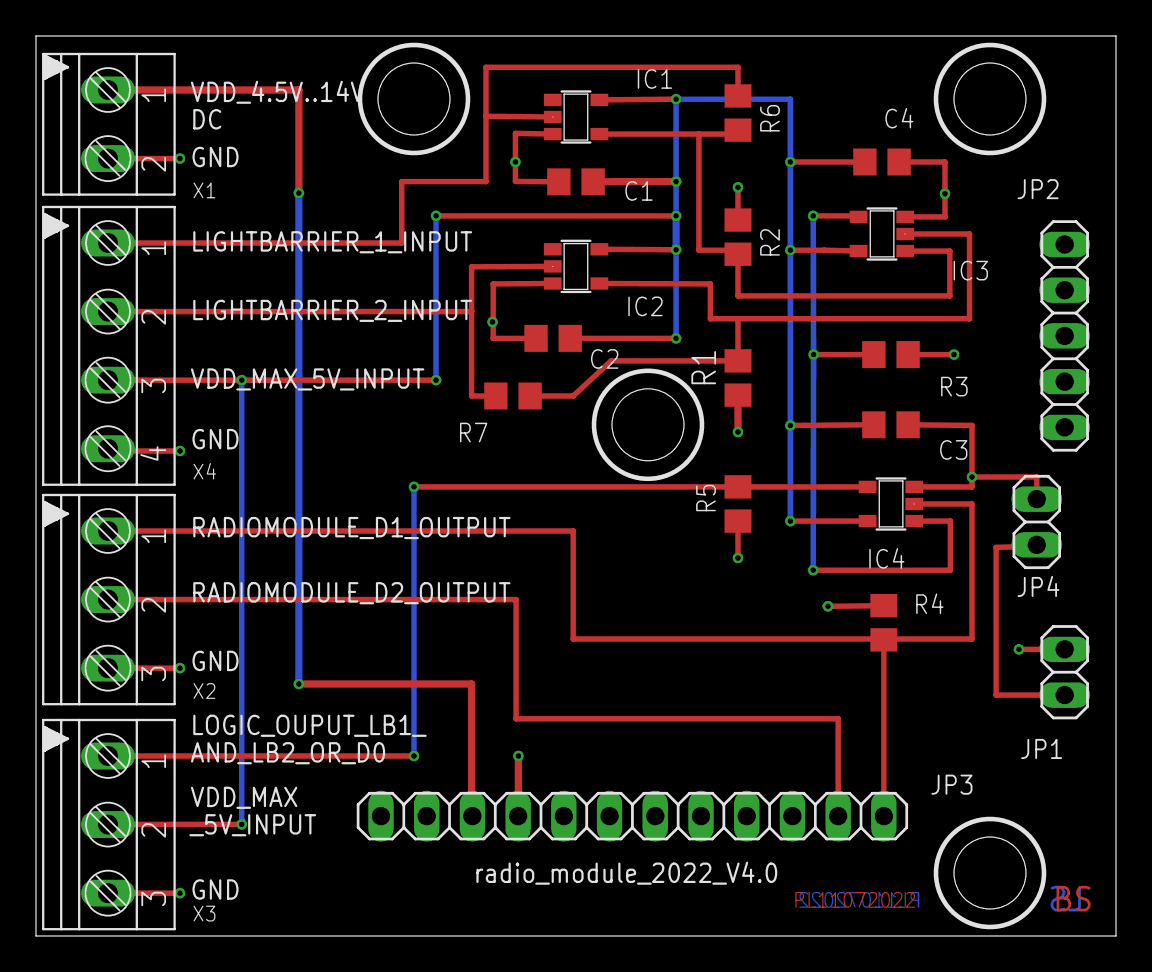
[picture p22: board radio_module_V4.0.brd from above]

Board: 4 copper layers, 60.0 x 50.0 mm, 23 parts (0 on the bottom side), 12 nets.

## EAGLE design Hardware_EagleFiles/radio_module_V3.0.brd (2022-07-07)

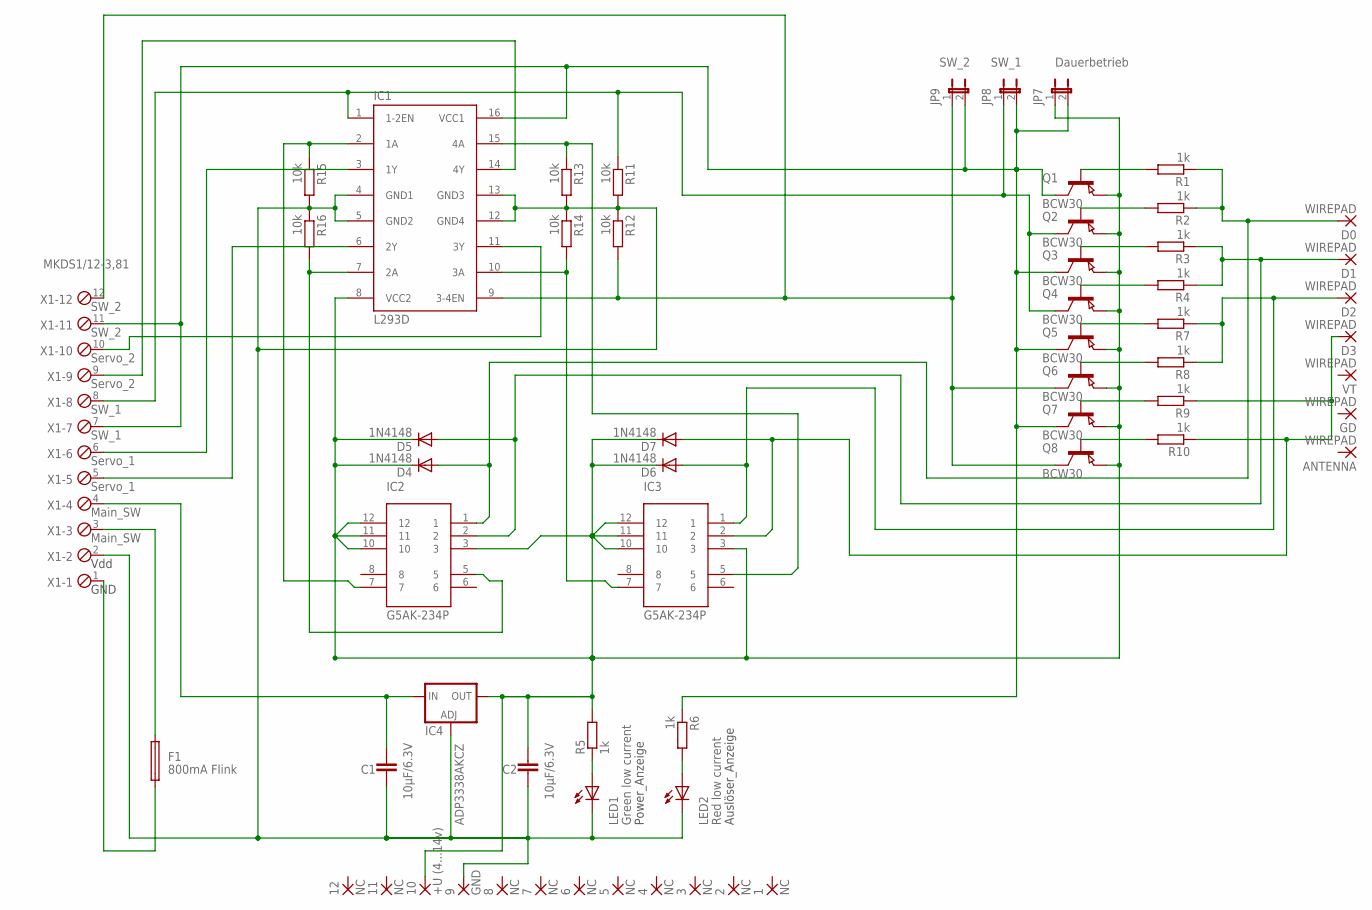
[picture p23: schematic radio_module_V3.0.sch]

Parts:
1, 2, 3, 4, 5, 6, 7, 8, 11, 12: NC; 1,6/0,9
9: GND; 1,6/0,9
10: +U (4...14v); 1,6/0,9
ANTENNA: WIREPAD; 1,6/0,9
C1, C2: 10µF/6.3V; C0805
D0, D1, D2, D3: WIREPAD; 1,6/0,9
D4, D5, D6, D7: 1N4148; DO35-7
F1: 800mA Flink; 19560
GD: WIREPAD; 1,6/0,9
IC1: L293D; DIL16
IC2, IC3: G5AK-234P
IC4: ADP3338AKCZ; SOT223
JP7: Dauerbetrieb; JP1
JP8: SW_1; JP1
JP9: SW_2; JP1
LED1: Green low current; LED3MM
LED2: Red low current; LED3MM
Q1, Q2, Q3, Q4, Q5, Q6, Q7, Q8: BCW30; SOT23
R1, R2, R3, R4, R5, R6, R7, R8, R9, R10: 1k; R0402
R11, R12, R13, R14, R15, R16: 10k; R0402
VT: WIREPAD; 1,6/0,9
X1: MKDS1/12-3,81; 12POL381

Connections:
GND: 9.1, C1.2, C2.2, IC1.4 (GND1), IC1.5 (GND2), IC1.12 (GND4), IC1.13 (GND3), IC4.1 (ADJ), LED1.K (C), LED2.K (C), R11.2, R12.1, R13.2, R14.1, R15.2, R16.1, X1.2
unnamed: IC1.3 (1Y), X1.6
unnamed: IC1.6 (2Y), X1.5
unnamed: IC1.7 (2A), IC2.5, R16.2
unnamed: IC1.11 (3Y), X1.10
unnamed: Q1.1 (B), R1.2
unnamed: Q3.1 (B), R3.2
unnamed: Q5.1 (B), R7.2
unnamed: Q7.1 (B), R9.2
unnamed: Q2.1 (B), R2.2
unnamed: Q4.1 (B), R4.2
unnamed: Q6.1 (B), R8.2
unnamed: Q8.1 (B), R10.2
unnamed: IC1.16 (VCC1), JP7.2, JP8.2, JP9.2, Q1.3 (C), Q3.3 (C), Q5.3 (C), Q7.3 (C), R6.1, X1.7, X1.11
unnamed: IC1.2 (1A), IC2.7, R15.1
unnamed: D0.1, D4.A, IC2.1, R1.1, R2.1
unnamed: LED2.A, R6.2
unnamed: F1.1, X1.1
unnamed: D1.1, D5.A, IC2.2, R3.1, R4.1
unnamed: IC1.14 (4Y), X1.9
unnamed: F1.2, X1.3
unnamed: D3.1, D7.A, IC3.2, R9.1, R10.1
unnamed: IC1.10 (3A), IC3.7, R14.2
unnamed: IC1.15 (4A), IC3.5, R13.1
unnamed: C1.1, IC4.3 (IN), X1.4
unnamed: LED1.A, R5.1
unnamed: D2.1, D6.A, IC3.1, R7.1, R8.1
unnamed: IC1.1 (1-2EN), JP8.1, Q2.3 (C), Q4.3 (C), R11.1, X1.8
unnamed: IC1.9 (3-4EN), JP9.1, Q6.3 (C), Q8.3 (C), R12.2, X1.12
VDD: 10.1, C2.1, D4.C, D5.C, D6.C, D7.C, IC1.8 (VCC2), IC2.3, IC2.10, IC2.11, IC2.12, IC3.3, IC3.10, IC3.11, IC3.12, IC4.4 (OUT), JP7.1, Q1.2 (E), Q2.2 (E), Q3.2 (E), Q4.2 (E), Q5.2 (E), Q6.2 (E), Q7.2 (E), Q8.2 (E), R5.2

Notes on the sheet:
Vdd
GND
SW_1
SW_2
Auslöser_Anzeige
Power_Anzeige
Main_SW
Servo_1
Servo_2

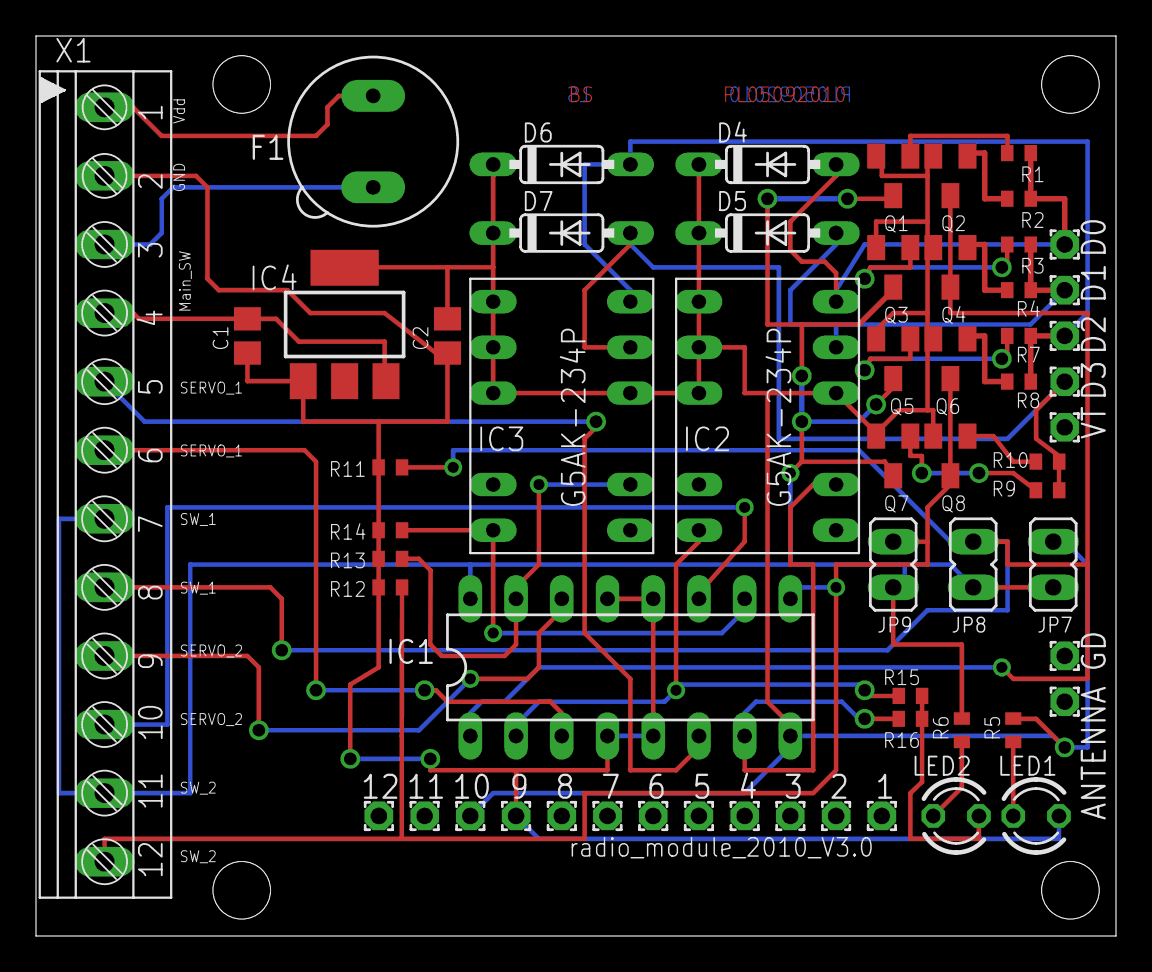
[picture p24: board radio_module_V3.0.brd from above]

Board: 2 copper layers, 60.0 x 50.0 mm, 60 parts (0 on the bottom side), 30 nets.
